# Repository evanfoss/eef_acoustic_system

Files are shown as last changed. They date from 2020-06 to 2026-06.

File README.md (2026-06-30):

# epl_acoustic_system
Distortion Products assay coupler

This is my personal fork of the original project
https://github.com/EPL-Engineering/epl_acoustic_system

TLDR; You want one and you don't want to build it? Ok Contact me.

You want to build one. Ok, I suggest the cui_driver version fitted with the db_driver/round2rect_fixture-Body.stl 3D printed adapter for the db driver to fit it. 

What is the process of making one of these like?
* buy all the parts for this project and
https://github.com/evanfoss/eef_acousticsyscable
https://github.com/evanfoss/eef_acousticsysmic
* cut and polish the fine stainless steel tubes to fit into the nose of the acoustic system.
* precision ream the holes in the 3D printed body of the device.
* precision align, and insert the tiny cut and polished tubes. Be sure to epoxy them with "2 Ton" epoxy or other similar hydrophobic slow cure adheasive. Do not get excess epoxy in the acoustic paths.
* insert db drivers into adapters and solder wires to them.
* insert the driver assemblies into the acoustic system body remembering to peel the plastic off the adheasive first.
* solder the wires to the connector. (again follow diagram)

What are all these files?

calibration - This is a calibration coupler for the device to a 1/4" microphone for calibration. While the use of a 1/8" microphone is prefered for calibration a simple to produce calibrator for that purpose is not yet available. This was designed by Ishmael.

pe275-010_driver - This version has great performance but it requires the pe275-010 tweeter from Parts-Express which is no longer available. This was a redesign of the cui_driver design done by Mike Ravicz with the assistance of the MGH Model Shop.

cui_drivers - This version is the last one EPL (Eaton Peabody Lab) used before the pe275-010 tweeter was found. The CUI driver has good max SPL but it isn't as even in frequency response because of breakup of the vibrational modes on the speaker cone. This was designed by Ishmael, Chis, Mike, using input from various parties.

db_driver - This contains both a version I designed clean sheet that has some cross talk issues. More importantly it contains the adapters needed to fit the db driver (which I believe is for cellphone speakers) into the cui_drivers 3D printed body. That is the one I currently produce on request. The smaller size of the driver means vibrational modes are not as much of a factor because it can be more rigid but the small size means it is more dependent on one time use only gasketting to reach higher SPL levels. Ishmael found the driver and I did the rest of the work.

nosepiece - Ishmael designed this precision machinable nose piece. Manufacturing this part requires a precision lathe for small parts and the ability to cut or better grind very small features.

wiring - This is the common wiring between all the acoustic systems here. Again Ishmael's handy work.

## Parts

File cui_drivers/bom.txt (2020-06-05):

Parts
Quant	Mfg #		Mfg.	Dist #		Distributor		Description
1	N.A.		Unknown	8987K24		McMaster Carr		304 Stainless Steel Tubing 0.12" OD, 0.01" Wall Thickness
1	N.A.		Unknown	8987K44		McMaster Carr		304 Stainless Steel Tubing 0.058" OD, 0.005" Wall Thickness
1	N.A.		Unknown	66215A24	McMaster Carr		Structural Adhesive Devcon, 2 Ton Epoxy, 1.69 oz., Cartridge
1	N.A.		Unknown	8974K22		McMaster Carr		Multipurpose 6061 Aluminum 1/4" Diameter
1	22-11-2042	Molex	WM2702-ND	Digikey			4 position 0.1" spaced male connector with ramp and rib

Tools
Quant	Dist#		Dist			Description
1	3087A33		McMaster Carr		High-Speed Steel Round-Shank Reamer Oversized, 0.2510" Reamer Diameter
1	8930A45		McMaster Carr		High-Speed Steel Round-Shank Reamer 31 Wire Gauge

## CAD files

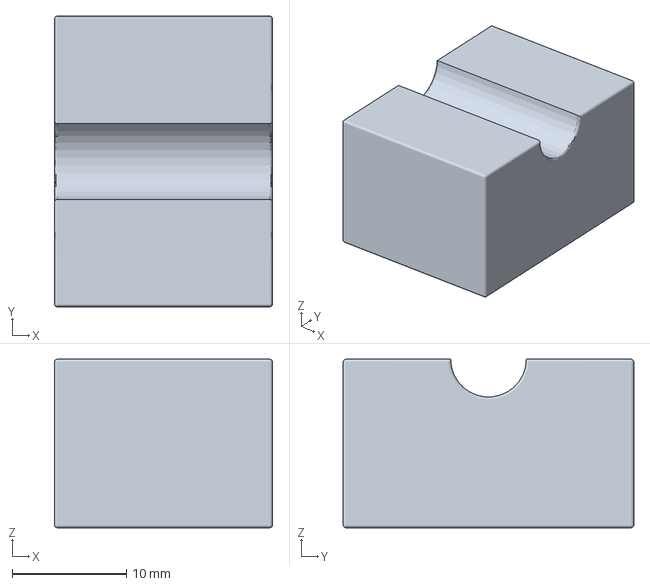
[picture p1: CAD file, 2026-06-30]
calibration/calfixture-Body_support2.3mf
19.1 x 25.4 x 14.7 mm

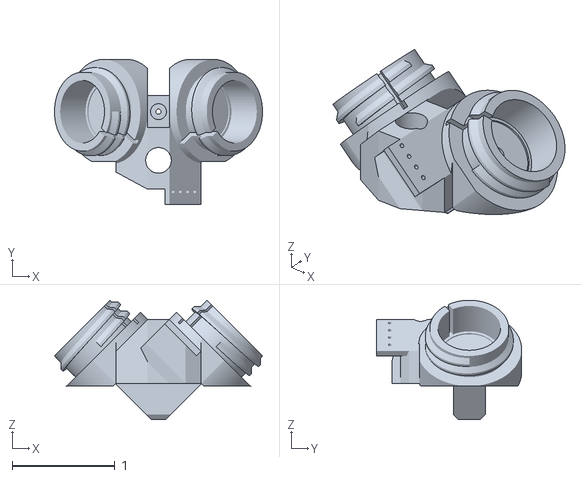
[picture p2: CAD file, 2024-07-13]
cui_drivers/Material_Body_v2_NewBody_Feb2009_REV-B-edit by steve.stl
2.03 x 1.42 x 1.17

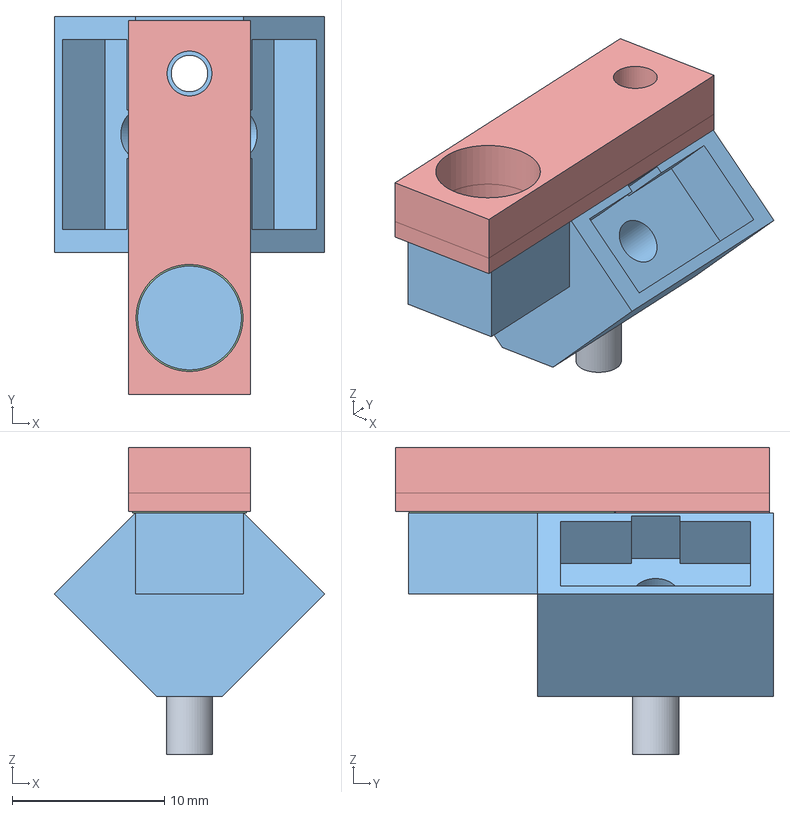
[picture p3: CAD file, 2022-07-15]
db_driver/acousticsys1.FCStd
17.8 x 24.8 x 20.2 mm
nose tube
probe tube
plastic_nose
cover

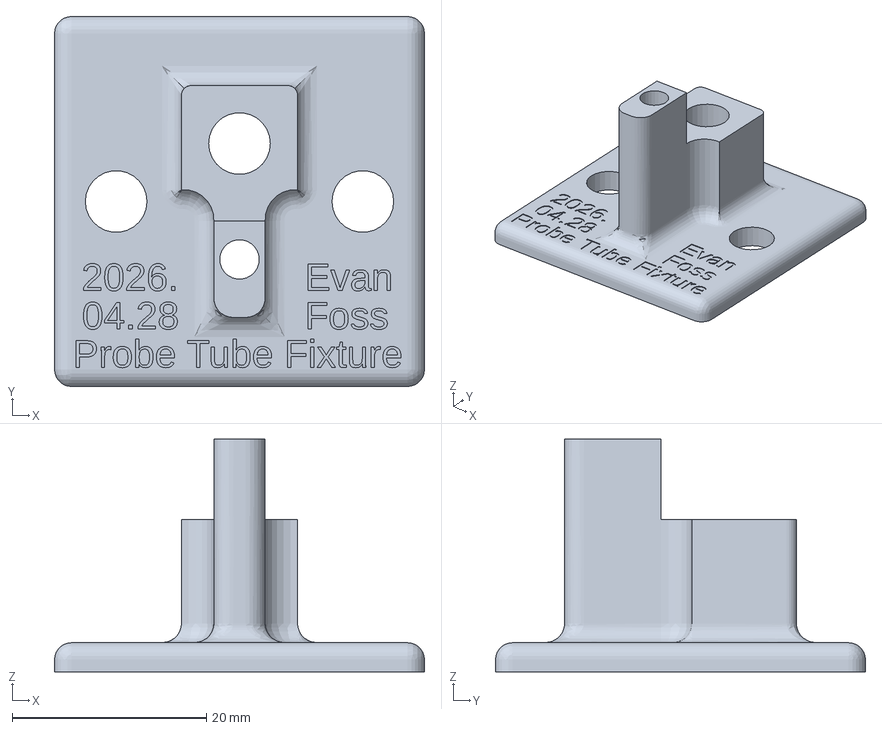
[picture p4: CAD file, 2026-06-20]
fixtures/tubingreameralignment-Body_fixture.3mf
38.1 x 38.1 x 24.0 mm

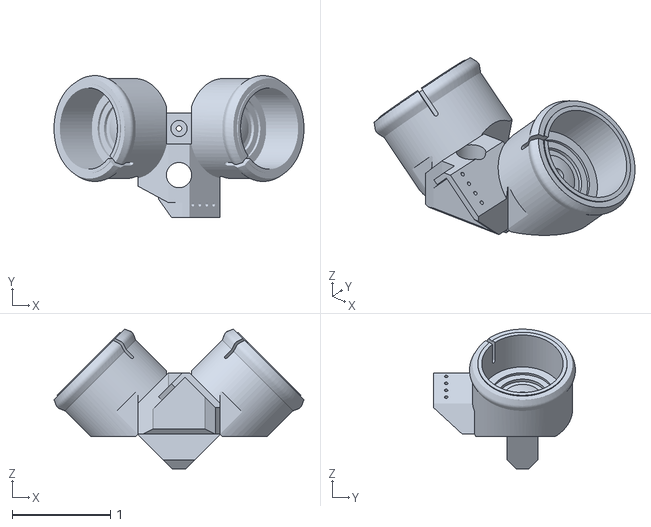
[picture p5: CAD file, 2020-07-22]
pe275-010_driver/Source2014A001.STL
2.55 x 1.45 x 1.43

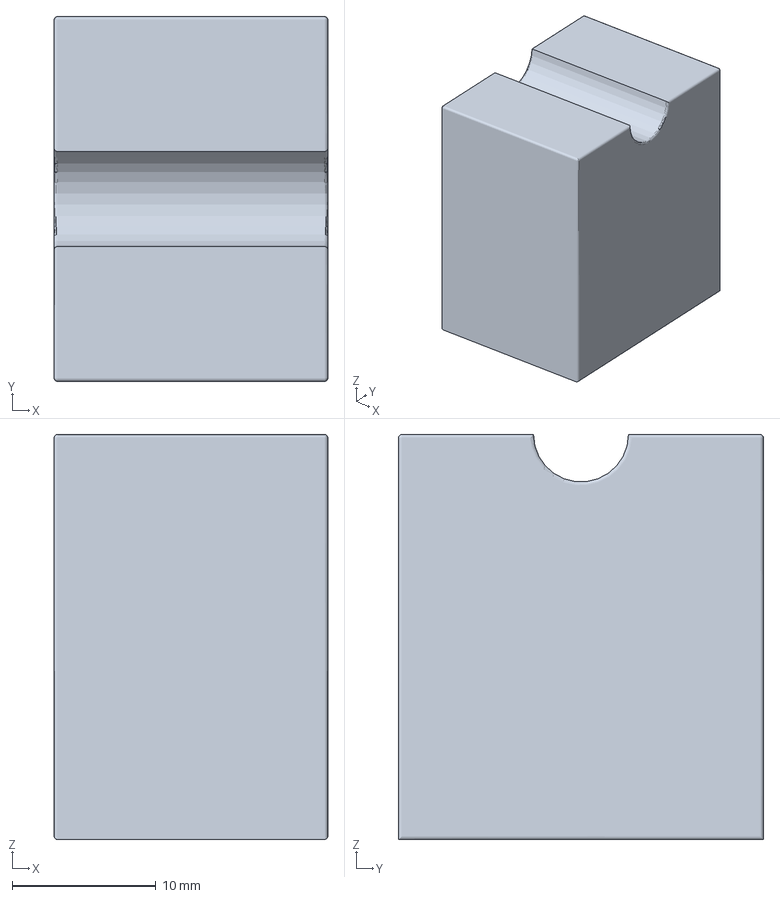
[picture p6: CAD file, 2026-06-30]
calibration/calfixture-Body_support3.3mf
19.0 x 25.4 x 28.2 mm

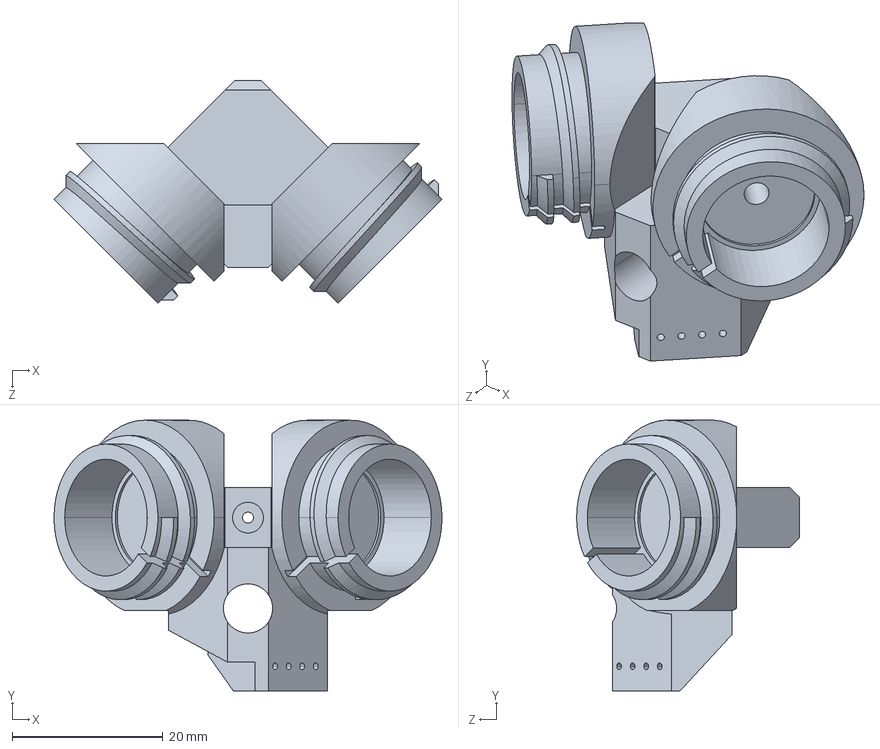
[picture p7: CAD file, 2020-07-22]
cui_drivers/Material_Body_v2_NewBody_Nov2009_REV-D_STEPAP203.STEP
51.5 x 36.0 x 29.6 mm

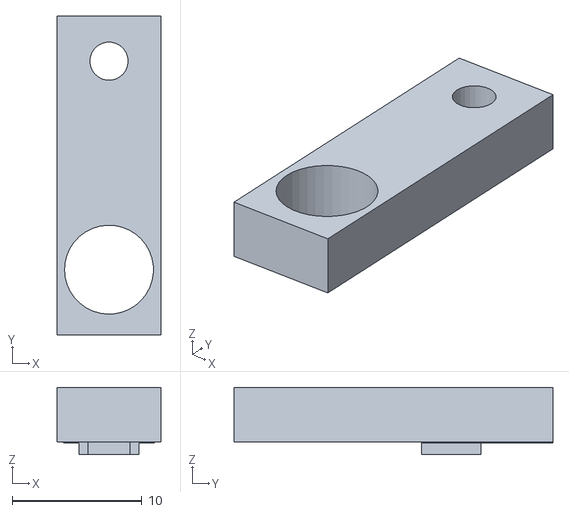
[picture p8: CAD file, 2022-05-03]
db_driver/acousticsys1-cover.stl
8.00 x 24.6 x 5.20

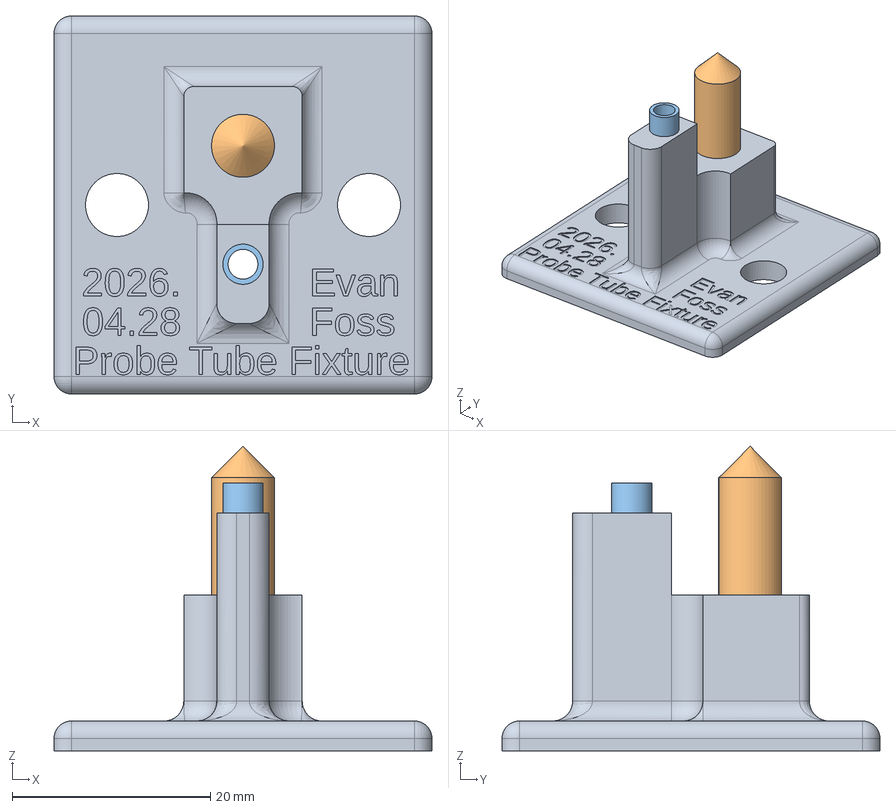
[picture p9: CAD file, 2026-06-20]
fixtures/tubingreameralignment.FCStd
38.1 x 38.1 x 30.7 mm
Body_fixture
Body_mountingrod
Body_probetube

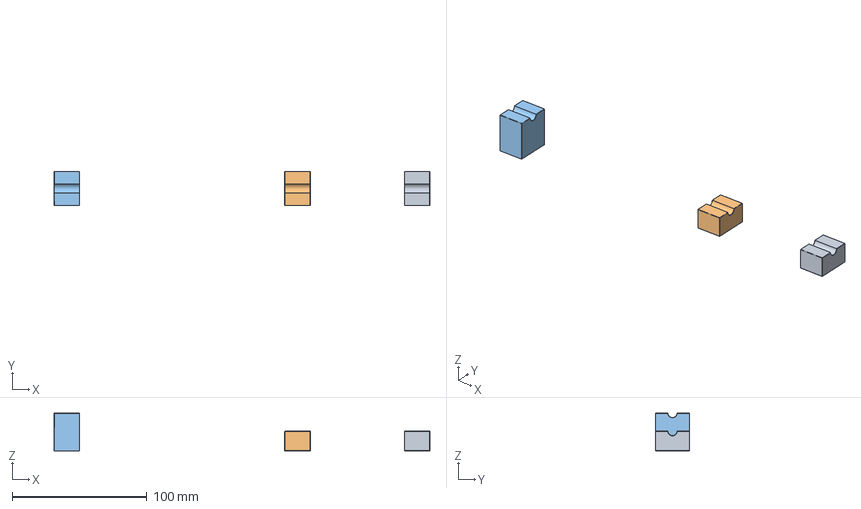
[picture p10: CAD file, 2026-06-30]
calibration/calfixture.FCStd
279.4 x 25.4 x 28.2 mm
Body_support1
Body_support2
Body_support3

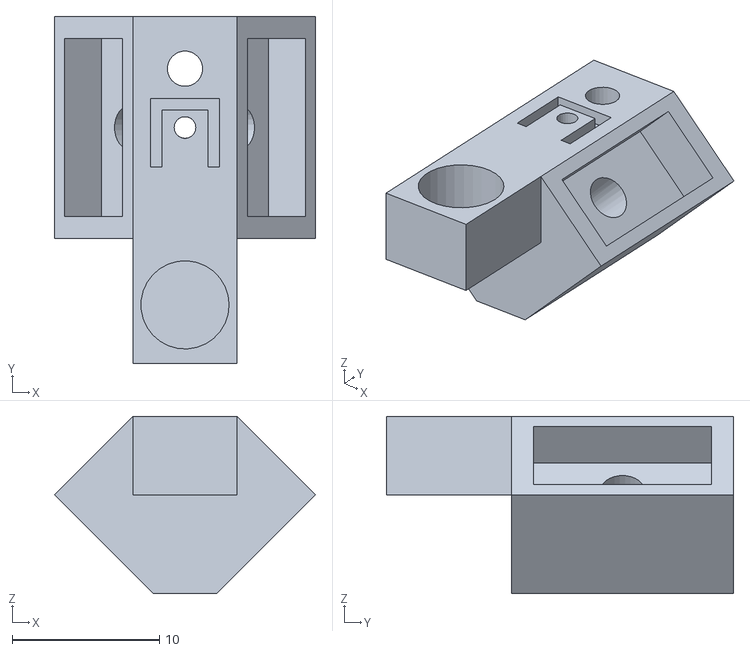
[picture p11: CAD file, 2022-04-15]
db_driver/acousticsys1-plastic_nose.stl
17.8 x 23.6 x 12.1

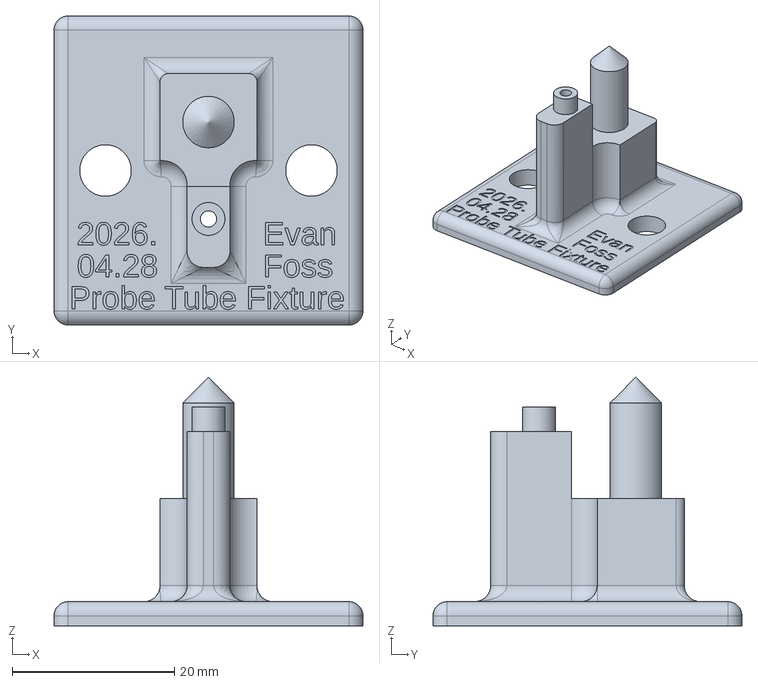
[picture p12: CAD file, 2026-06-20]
fixtures/tubingreameralignment-merged-junk.FCStd
38.1 x 38.1 x 30.7 mm

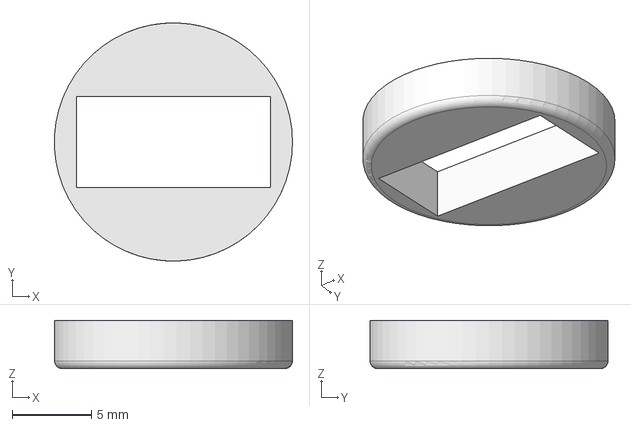
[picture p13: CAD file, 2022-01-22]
db_driver/round2rect_fixture.FCStd
15.0 x 15.0 x 3.05 mm

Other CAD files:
cui_drivers/Material_Body_v2_NewBody_Feb2009_REV-B.STL
calibration/calfixture-Body_support1.3mf
fixtures/tubingreameralignment-merged-Body_fixture.3mf
db_driver/round2rect_fixture-Body.stl
fixtures/tubingreameralignment-merged.FCStd
fixtures/micport_reamer.FCStd
fixtures/tubingreameralignment-Body.3mf

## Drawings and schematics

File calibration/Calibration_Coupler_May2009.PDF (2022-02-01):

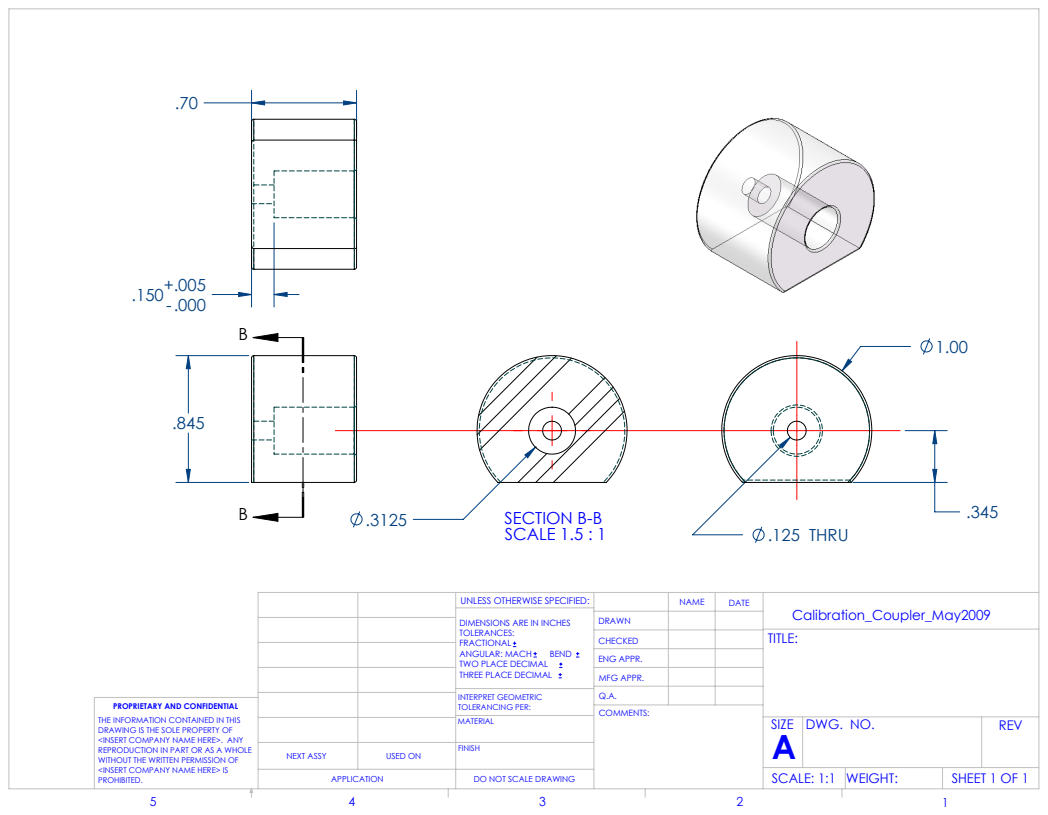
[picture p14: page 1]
.125 THRU; SECTION B-B; SCALE 1.5 : 1; SHEET 1 OF 1; SCALE: 1:1 WEIGHT:; DWG. NO.; REV; MFG APPR.; ENG APPR.; INTERPRET GEOMETRIC TOLERANCING PER:; ANGULAR: MACH; BEND; NEXT ASSY; USED ON

UNLESS OTHERWISE SPECIFIED:

DIMENSIONS ARE IN INCHES
TOLERANCES:
FRACTIONAL
TWO PLACE DECIMAL
THREE PLACE DECIMAL

PROPRIETARY AND CONFIDENTIAL
THE INFORMATION CONTAINED IN THIS
DRAWING IS THE SOLE PROPERTY OF
<INSERT COMPANY NAME HERE>. ANY
REPRODUCTION IN PART OR AS A WHOLE
WITHOUT THE WRITTEN PERMISSION OF
<INSERT COMPANY NAME HERE> IS
PROHIBITED.

DO NOT SCALE DRAWING

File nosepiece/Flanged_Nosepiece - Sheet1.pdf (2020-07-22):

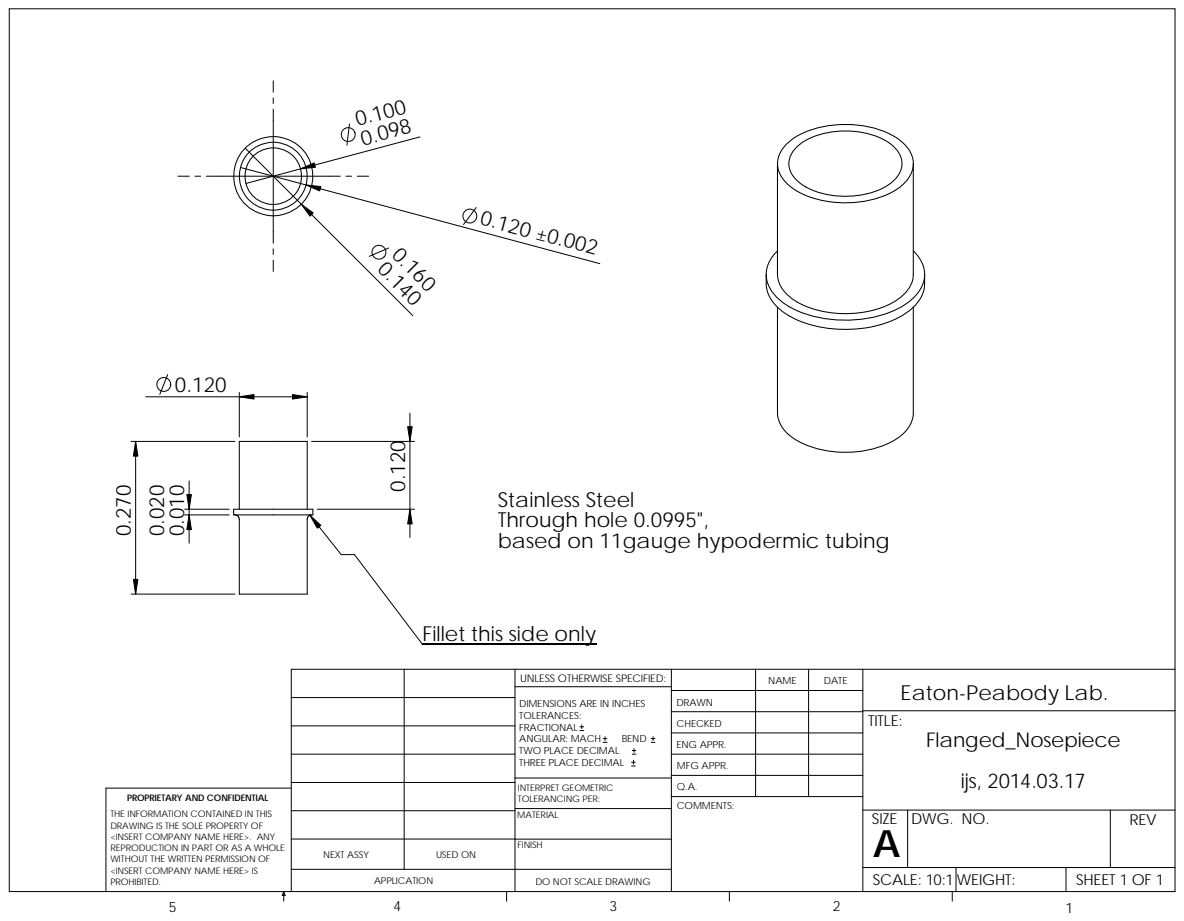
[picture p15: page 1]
BEND; COMMENTS:

Stainless Steel
Through hole 0.0995",
based on 11gauge hypodermic tubing

Fillet this side only

UNLESS OTHERWISE SPECIFIED: | | NAME | DATE | Eaton-Peabody Lab.

DRAWN
CHECKED | | | TITLE: Flanged_Nosepiece ijs, 2014.03.17

DIMENSIONS ARE IN INCHES
TOLERANCES:
FRACTIONAL
ANGULAR: MACH
ENG APPR. TWO PLACE DECIMAL
THREE PLACE DECIMAL

MFG APPR.

INTERPRET GEOMETRIC TOLERANCING PER: | Q.A.

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

MATERIAL | | SIZE A | DWG. NO. | REV

NEXT ASSY | USED ON | FINISH
APPLICATION | DO NOT SCALE DRAWING | | SCALE: 10:1 WEIGHT: | | SHEET 1 OF 1

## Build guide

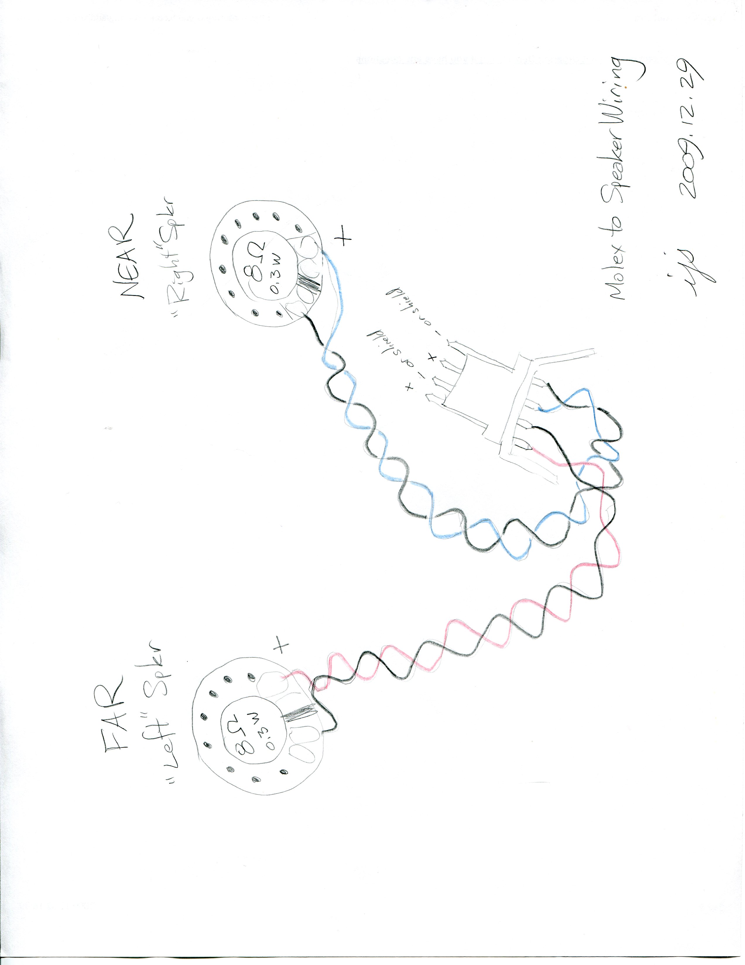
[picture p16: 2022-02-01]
wiring/DPOAE_Molex_to_Speakers_img004.jpg

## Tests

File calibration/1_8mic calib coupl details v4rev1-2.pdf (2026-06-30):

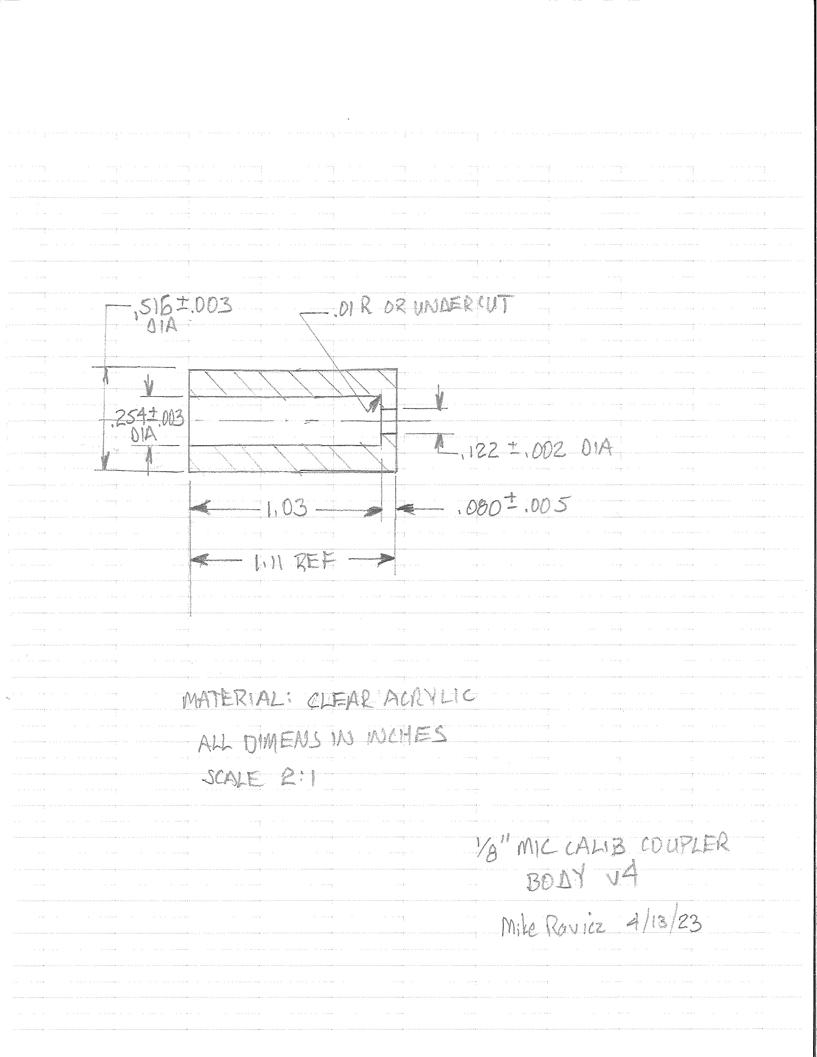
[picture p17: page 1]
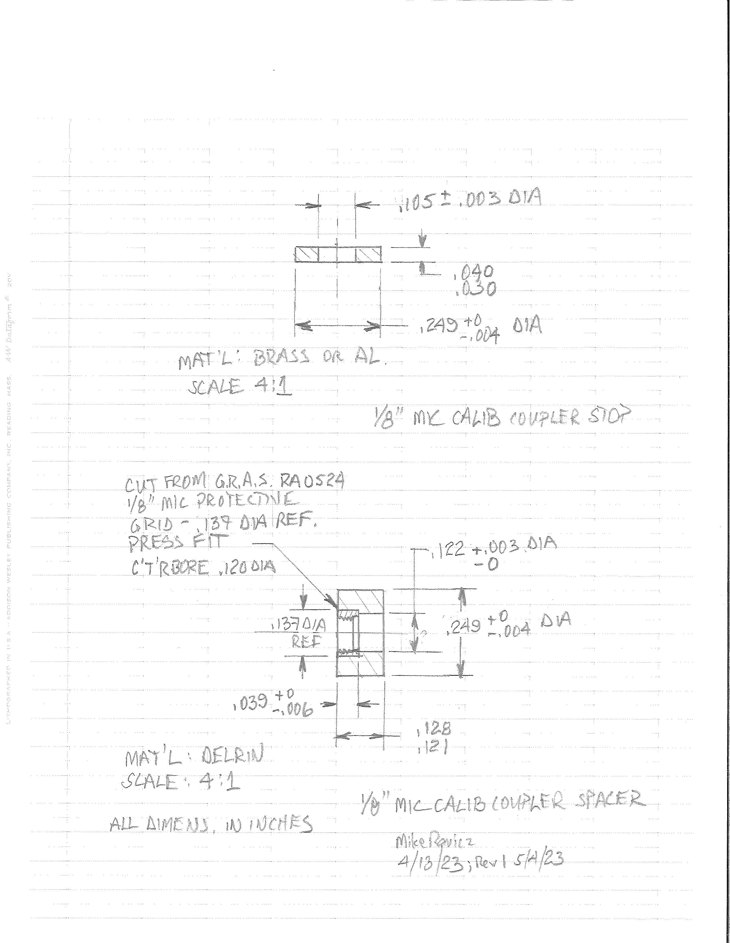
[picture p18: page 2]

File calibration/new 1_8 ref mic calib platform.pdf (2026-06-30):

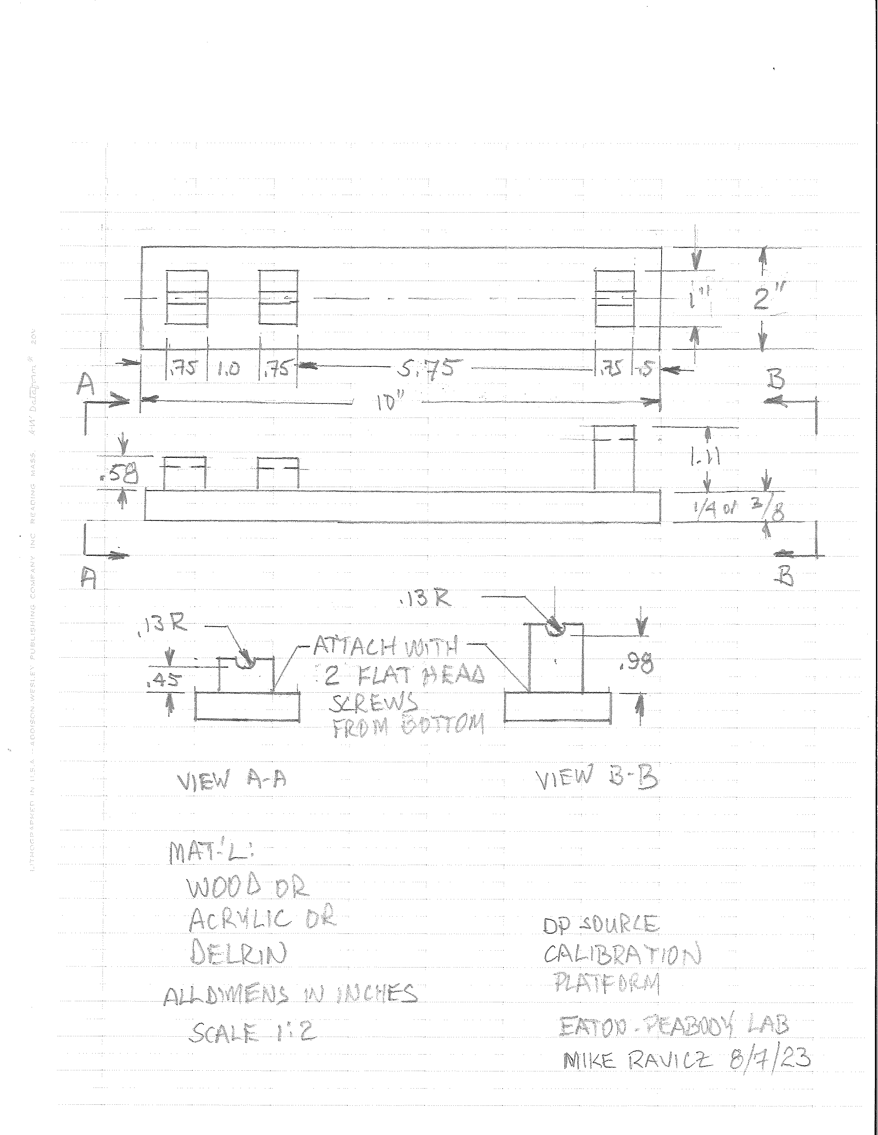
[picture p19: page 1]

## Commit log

2020-07-22 add: stl and step files for the printable parts
    [Material_Body_v2_NewBody_Feb2009_REV-B.STL, Material_Body_v2_NewBody_Nov2009_REV-D_STEPAP203.STEP, Source2014A001.STL]
2022-01-22 add: db_driver prototype work in progress
    [acousticsys.FCStd, acousticsys1.FCStd, adapterrectoround.gbl, adapterrectoround.gbo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]
2022-01-31 add: cleaning
    [acousticsys.FCStd, test.FCStd]
2022-01-31 add: note about the distance between holes on the acoustic system
2022-02-01 add: missing files from earlier
    [acousticsys1.FCStd]
2022-02-07 add: better dimensioning
    [acousticsys1.FCStd]
2022-02-16 add: speaker cavities with acoustic paths
    [acousticsys1-20220207-1.FCStd, acousticsys1.FCStd]
2022-02-16 add: speaker outline
    [acousticsys1.FCStd]
2022-02-16 add: mounting post block and hole
    [acousticsys1.FCStd]
2022-03-28 rebuild: backcover
    [acousticsys1-addedthumbscrew.FCStd, acousticsys1-mic added.FCStd, acousticsys1-mic addedproperly.FCStd, acousticsys1-solidmiccover.FCStd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]
2022-03-28 del: removed layers that freecad wouldn't let me subtract
    [acousticsys1.FCStd]
2022-03-28 add: improved mic holder outline
    [acousticsys1.FCStd]
2022-03-28 add: back cover done
    [acousticsys1.FCStd]
2022-03-28 cleanup: removed junk
    [acousticsys1-20220207-1.FCStd, acousticsys1-addedthumbscrew.FCStd, acousticsys1-mic added.FCStd, acousticsys1-mic addedproperly.FCStd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]
2022-04-15 fix: body mounting rode hole was too small
    [acousticsys1-cover.stl, acousticsys1-plastic_nose.stl, acousticsys1.FCStd]
2022-05-03 fix: microphone cover revised to solve issues with 1/4 rod
    [acousticsys1-cover.stl, acousticsys1.FCStd]
2022-07-08 add: corrected mounting rod hole diameter
    [acousticsys1-cover.stl, acousticsys1-plastic_nose.stl, acousticsys1.FCStd, adapterrectoround.gbl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]
2022-07-08 fix: added 0.4mm to l and w of speaker cavities
    [acousticsys1.FCStd]
2022-07-15 add: thumbscrew head outline and speaker slots
    [acousticsys1.FCStd]
2024-07-13 add: steve helpfully made a change that I requested to require reaming of the microphone probe hole diameter
    [Material_Body_v2_NewBody_Feb2009_REV-B-edit by steve.stl]
2024-07-13 move: the 2009 is currently in use the db driver but was made for CUI
    [Material_Body_v2_NewBody_Feb2009_REV-B-edit by steve.stl]
2025-06-20 add: mic port reaming fixture
    [micport_reamer.FCStd]
2025-10-05 add: labels to the mic port reamer
    [micport_reamer.FCStd]
2026-06-20 add: fixtures for reaming various parts
    [tubingreameralignment-Body.3mf, tubingreameralignment-Body_fixture.3mf, tubingreameralignment-merged-Body_fixture.3mf, tubingreameralignment-merged-junk.FCStd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]
2026-06-27 add: calibration fixture (warning support spacing wrong)
    [calfixture-Body_support1.3mf, calfixture-Body_support2.3mf, calfixture-Body_support3.3mf, calfixture.FCStd]
2026-06-30 fix: revised calibration files + pdf from Mike
    [calfixture-Body_support1.3mf, calfixture-Body_support2.3mf, calfixture-Body_support3.3mf, calfixture.FCStd]
